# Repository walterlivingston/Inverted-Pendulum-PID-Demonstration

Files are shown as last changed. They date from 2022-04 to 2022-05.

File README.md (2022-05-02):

# Inverted Pendulum PID Demonstration
This was the final project for Applied Mechatronics(MECH 5970) at Auburn University. The project was meant to reflect the four major concepts learned in the class: Sensing, Actuation, Computation, and Mechanical Design.  For this project, an inverted pendulum controlled by a variable PID controller was chosen.  This project was meant to be a demonstration for the professor's Systems & Dynamic Controls(MECH 3140) course.

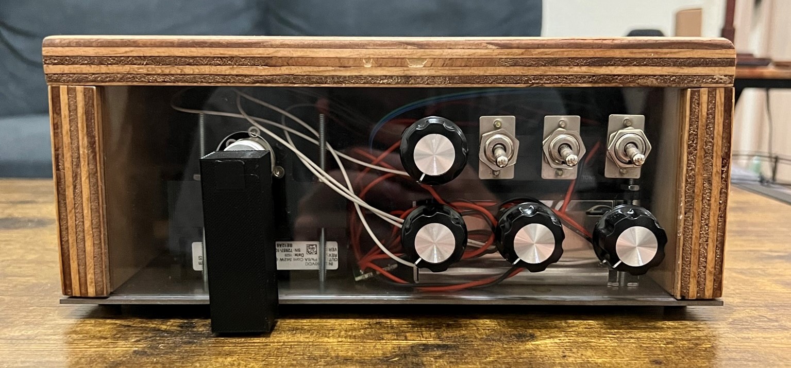
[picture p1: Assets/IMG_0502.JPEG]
Inverted Pendulum Controls Demonstration


## Project Video
Project Video (https://youtu.be/PuW2v3_iuz4)

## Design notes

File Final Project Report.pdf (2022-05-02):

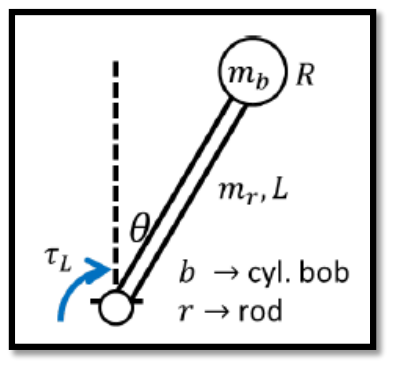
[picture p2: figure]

## Final Project 4: Inverted Pendulum Controls Demonstration

Applied Mechatronics (MECH 5970-019) April 29, 2022
Walter Livingston | Matthew Covington
wbl0009 | mac0139

### Table of Contents

Team Photo | 4
Project Photos | 4
Project Demonstration Video | 7
Functional Summary | 7
Sensing | 7
Actuation | 8
Computation | 8
Mechanical Design | 9
Build Documentation | 10
Schematics and Drawings | 11
Assembly and Part Drawings | 11
LabVIEW Code & Explanation | 11
Improvements | 15
Structural | 15
Functional | 15
Appendix A: Assembly and Part Drawings | 17

### Table of Figures

Figure 1: Team Photo | 4
Figure 2: Front Panel 1 | 4
Figure 3: Front Panel 2 | 5
Figure 4: Back Panel | 5
Figure 5: Internals | 6
Figure 6: IPCD CAD Model | 11
Figure 7: LabVIEW Code | 12
Figure 8: LabVIEW UI | 12
Figure 9: Encoder Processing Snippet | 13
Figure 10: PID Calculations Snippet | 14
Figure 11: Input Filtering Snippet | 14

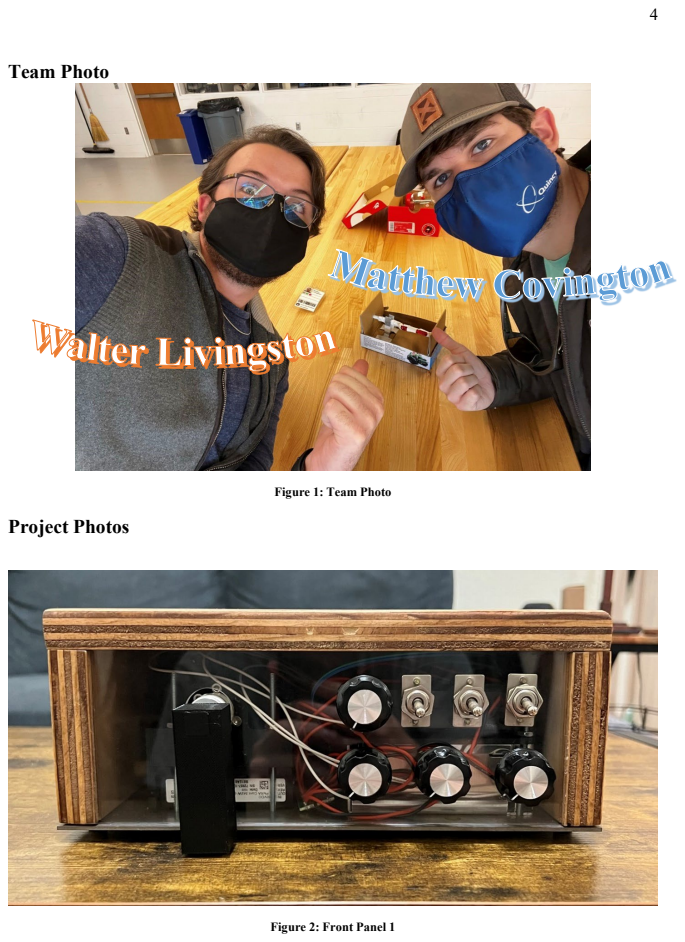
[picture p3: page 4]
Team Photo; Project Photos

Figure 1: Team Photo

Figure 2: Front Panel 1

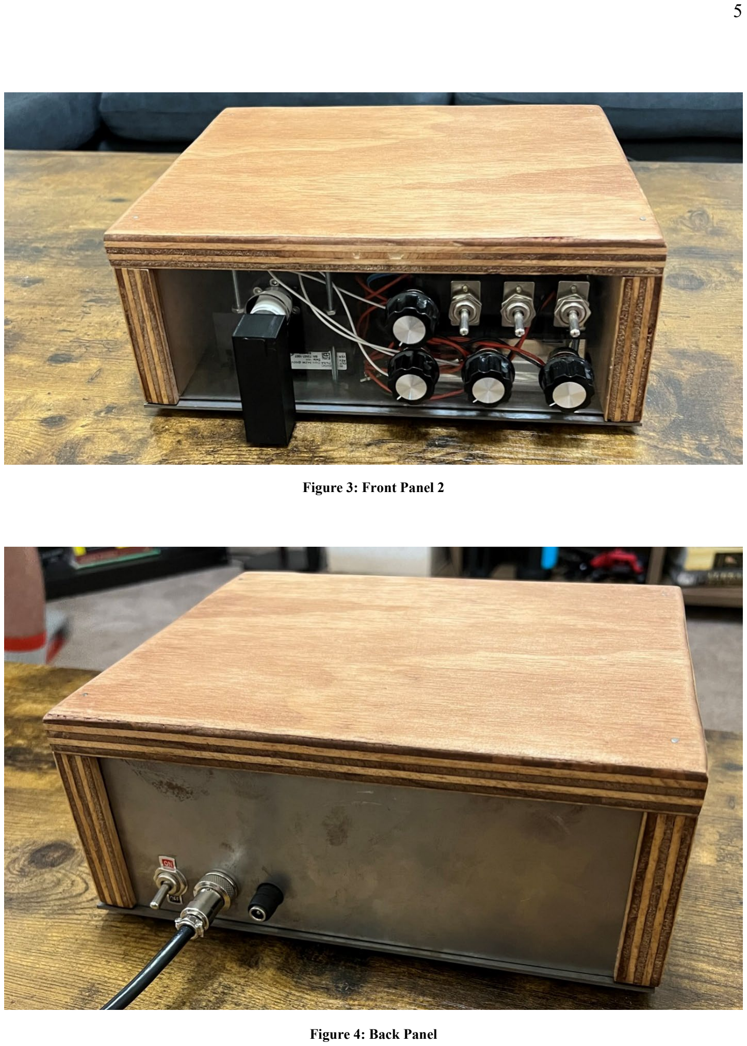
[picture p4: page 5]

Figure 3: Front Panel 2

Figure 4: Back Panel

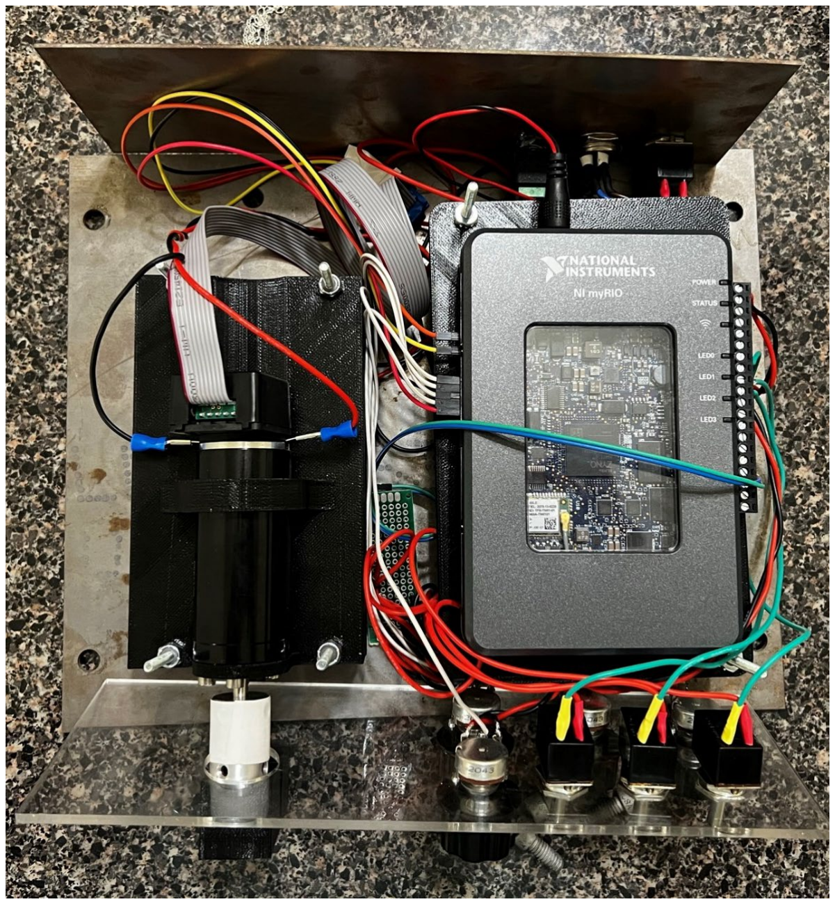
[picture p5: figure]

Figure 5: Internals

### Project Demonstration Video

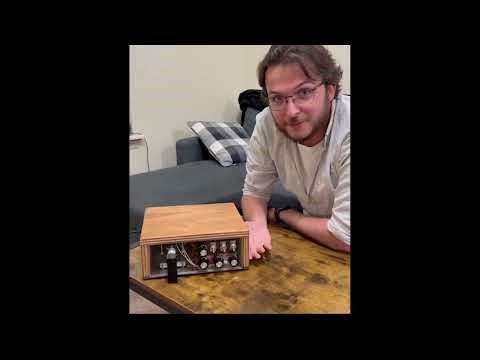
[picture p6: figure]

### Functional Summary

The IPCD’s (Inverted Pendulum Control’s Demonstration) main purpose it to demonstrate the effects of PID control on a dynamic system. This was accomplished by integrating the four founding concepts of this project: Sensing, Actuation, Computation, and Mechanical Design.
Sensing
The primary sensing implementation in this project was a digital encoder. We mounted a HEDL 5540 encoder to the back of the Maxon RE30 24V that will be discussed further in the Actuation section. This encoder had 500 counts per revolution, meaning that the counts had to be read and converted to degrees (or radians). This was accomplished utilizing the NI myRIO 1900 discussed further in Computation. This encoder’s reading acts as the feedback to close the control loop. Every loop of the program read the current angular position of the encoder, processed it based on user-defined gains, and output a control effort to the servo amp.
Another form of sensing in this project comes from the use of potentiometers as part of the user interface. Four potentiometers were used in all: one for the control setpoint, and the other three for the PID gains. A difficulty in this, is given that a potentiometer is an analog device, it is very susceptible to noise. Because the pendulum is meant to be reliable, noise in the user input is unacceptable. To improve reliability within the pendulum’s control, software-based Butterworth filters were used on each input to filter out most noise.

The last form of sensing utilized for this process would be the use of switches. This form of sensing is simplistic as switches are either on or off, and their functionality was written accordingly. If they were on, X happens and if not, Y happens.
Actuation
The actuation implementation within this project was a Maxon RE30 24V motor used in tandem with an AMC Brushless Servo Amp. The motor acts as the torque/control input to the inverted pendulum. The pendulum was mounted about its end to the motor shaft using a coupler. This allowed for sample calculations to be simple given the moment of inertia was comparable to a thin rod rotating about its end.
The servo amp is what allowed the motor to be driven with a -10V/10V analog output from the NI myRIO. The current gain for the amplifier was set at approximately 0.3A/V as this had been tested in Project 3 and provided good results. This gain also simplified the sample calculations, as some of them had already been completed for Project 3.
Computation
The computation in this project was performed by the NI myRIO 1900. This microcontroller uses the LabVIEW programming environment which contains a lot of useful, prebuilt functions for various tasks; some of which are specific to reading and writing from the myRIO. For this project, the National Instruments PID VI (Virtual Instrument) was originally implemented but was eventually replaced by custom PID calculations. The reason for this, is that for a reliable controller design, a full understanding of all the workings of the controller was desired as opposed to a “black box” of controls calculations.
One particular benefit of the myRIO that stands to be noted is its extremely high sampling rate and achievable loop rates. While the generic While Loop within LabVIEW is limited to a 1kHz loop rate, the Real-Time While Loop can achieve rates of up to 1MHz. The importance here is the fact that since digital sensing is used for the feedback loop of the inverted pendulum’s controller. This project is meant to be a demonstration for Dr. Rose’s Systems & Dynamic Control’s course, which deals primarily with the continuous domain. The encoder, and its digital readings, are within the discrete domain. To try and close the gap between these two forms of control, a high loop rate was desirable. The higher the loop rate, the smaller the discretization of readings, and the closer overall the pendulum’s response is to its continuous counterpart.
Within the myRIO programming, many functions and features are established. A general overview of this process is as follows: The myRIO takes in a counter input from the encoder. This counter input is converted to degrees and is compared to the setpoint, as measured by a potentiometer input, and error is calculated. This error is multiplied by a proportional gain, also set by a potentiometer. The derivative of this error is taken and multiplied by a derivative gain set by a potentiometer. The integral of this error is also taken and multiplied by an integral gain set by a potentiometer. With these three gains applied, they’re outputs are all summed together and provided to the Servo Amp as a control effort, or command voltage.

While the above process describes the PID controller used in this project, other features were implemented as well, and controlled by toggle switch inputs. Three additional functions were implemented. The first of which was a frequency input. When this is enabled, the controller outputs a sinusoid with an amplitude of 10 and a frequency set by the setpoint potentiometer. This allows the user to see how various PID gains would affect the frequency response at frequencies between 0 and 2 deg/s. This small range was used to prevent instabilities at all PID gains.
The next function implemented was anti-windup. An integral controller takes the area between the current position and setpoint and uses it to create a control effort to “close the gap.” In cases of large error, this can cause what is called windup. When the integral becomes so large, even when the error is closed, the integral controller is still exhibiting a control effort, which is now no longer decreasing error but increasing it. The anti-windup function reinitializes the integral to zero when it reaches saturation; for this project, saturation is 10/-10 as that is the output of the analog pins utilized on the myRIO.
The last function implemented was controls hold. This switch allows the user to pause the PID gains at their current values and turn the knobs without affect. For instance, if the IPCD is setup with only proportional gain, and the hold switch is turned on. The user can change all of the gains, and the pendulum will still only exhibit a proportional response. But as soon as the hold is turned off, the new gains will take effect and a new response can be observed. Mechanical Design
This project implements a wide variety of concepts lending to the Mechanical Design portion of this project. The first of which would be the mounting method for the motor.
The electrical components were mounted to the base plate of the control module. The base plate is made of 1/8” A36 steel. A 3D printed part was used to secure the DC motor atop the AMC Servo Amp. The part has a hole to allow for the shaft of the motor to pass through so it may be connected to a pendulum. It also has holes through which screws may be placed to ensure the motor does not move. To fasten this part to the base plate, holes in both parts are present, with four 3” bolts passing through both. The AMC Servo Amp is sandwiched between the motor mount and the baseplate, with the 3” bolts passing through the mounting cutouts on the motor driver. The pendulum arm and dowel are 3D printed parts; they are press fit together to allow for a secure connection. A cavity within the pendulum arm allows pennies to be press fit inside it as to raise the moment of inertia, which allows for easier control of the motor position. This cavity allows more weight in the pendulum arm, without making it longer. A coupler is used to connect the pendulum to the shaft of the DC motor.
A similar method is used to mount the myRIO and the power supply. A part was also printed for the myRIO to interface with, with two 3” bolts used to secure this to the mounting plate. The power supply is sandwiched between the motor mount and the baseplate, with the 3” bolts passing through mounting holes on the power supply. Power for the myRIO and the power supply are provided by two power ports mounted to the back plate of the IPCD. The back plate also has an on/off switch mounted to it. The backplate is made of 1/16” aluminum sheet metal.

The front plate is made of 0.117” clear acrylic. This material was used as a means of allowing users to view the inner workings of the IPCD. This front plate houses four potentiometers used as control gain and the position inputs. These are used by the myRIO to determine voltage output (control effort) to the DC motor. Along with potentiometers, toggle switches are also mounted to the front plate. These switches are used as the feature controls mentioned in Computation.
To encapsulate the device, 3/4” AC radiata pine is used for the side walls and top. This material was chosen for aesthetic purposes as the IPCD was meant to look like a vintage stereo. The side pieces are mounted to the base plate via rivet nuts and screws. The rivet nuts were pressure fit into the wood after drilling appropriately sized holes. The screws pass through the baseplate and thread into the rivet nuts, as well as they serve as feet for the device. The top is secure to the side walls by use of wood glue and finishing nails. Each of these pieces have 1/8” wide cutouts which the front and back pieces slide into, ensuring they will not move without having to mount them. This method allows the front and back pieces to be replaced or altered easily.

### Build Documentation

All files and models associated with this project can be found in the following GitHub repository: https://github.com/walterlivingston/Inverted-Pendulum-PID-Demonstration

Schematics and Drawings

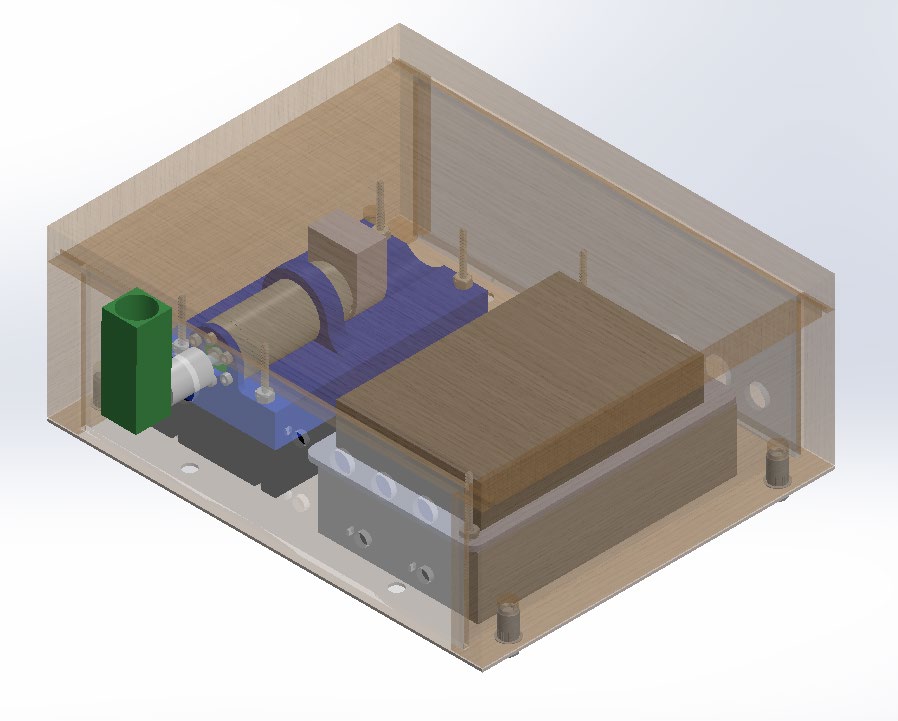
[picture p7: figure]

Figure 6: IPCD CAD Model
Assembly and Part Drawings
The drawing for each assembly (control module, motor mounting assembly, and pendulum) as well as part drawings designed for this project can be found in Appendix A.
LabVIEW Code & Explanation
The code implemented on the myRIO can be seen below in Figure 2. This visual code was written in the LabVIEW Environment. The box around everything here is known as a Real Time While Loop and in this project, was run at a loop rate of 1kHz.

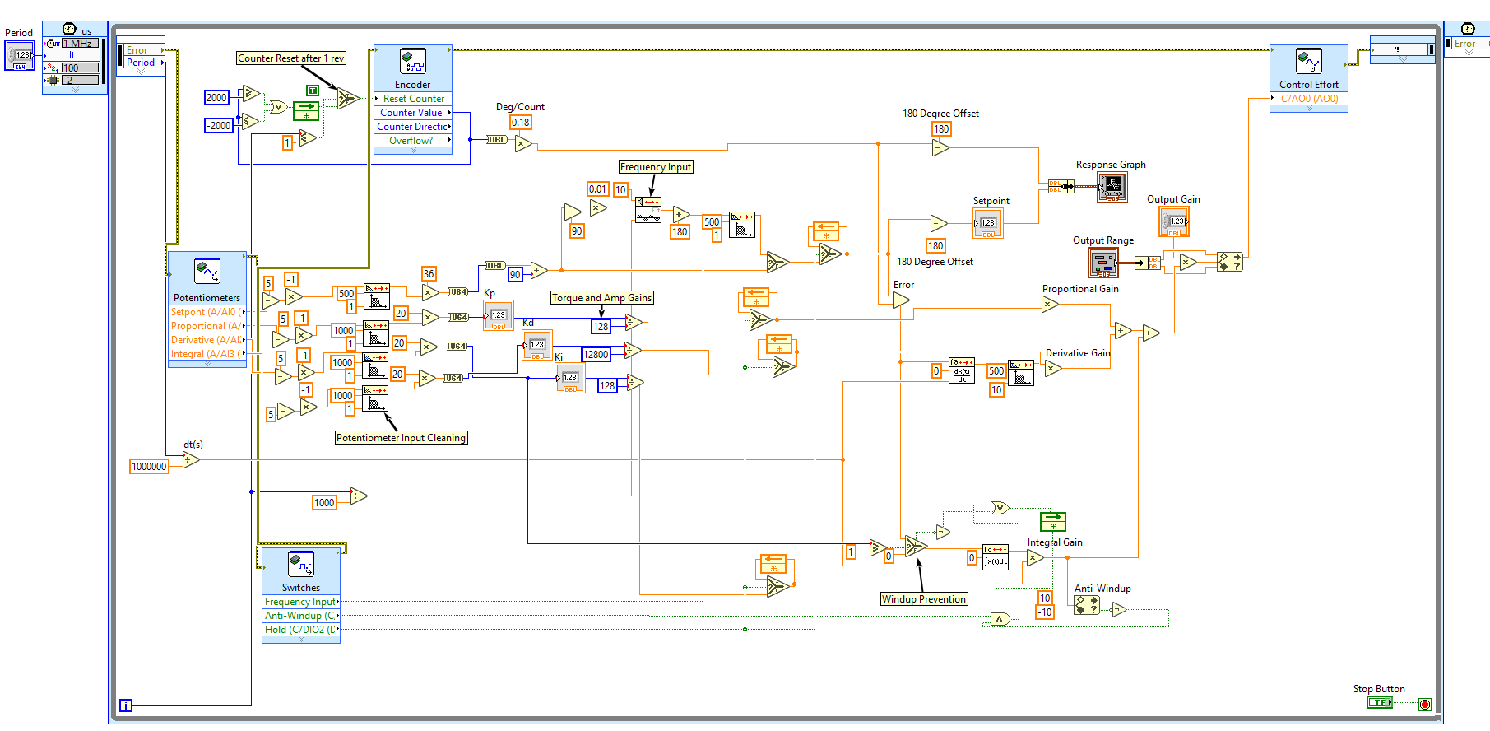
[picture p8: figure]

Figure 7: LabVIEW Code
The UI used to troubleshoot this project can also be seen in Figure 3. This includes a response graph showing the setpoint and the pendulum’s position. It also contains indicators for the setpoint and PID gains. There are controls for an optional output gain (not used in the final version), the period of the loop, and inputs for an output range. These were also useful in troubleshooting the code shown above in Figure 2.

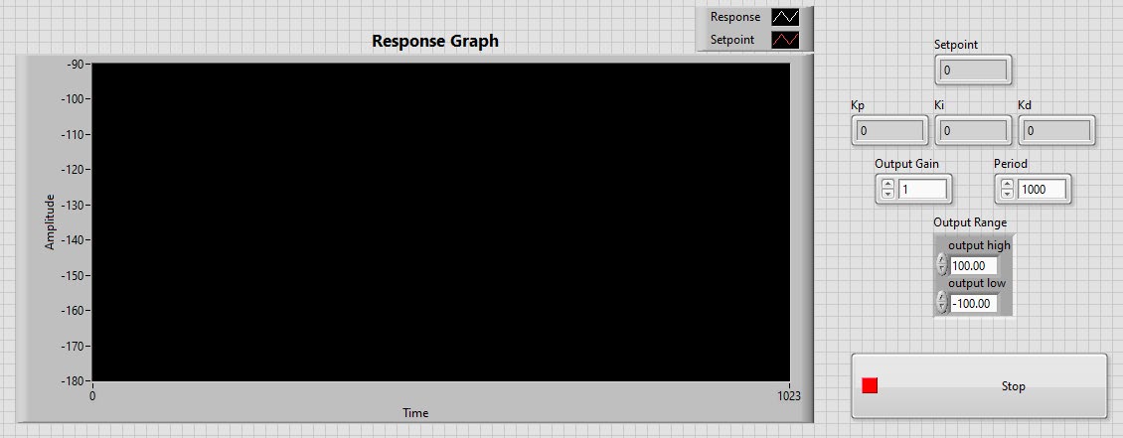
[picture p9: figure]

Figure 8: LabVIEW UI
The encoder readings were handled by the code snippet shown in Figure 4. This takes the encoder value and compares it to -/+ 2000. The reason for this is the HEDL 5400 encoder used in this project has a counts per revolution of 500. This being a quadrature encoder, that means that the myRIO is reading 4 times the counts per revolution, that being 2000. This comparison tells the myRIO to reset the counter if the encoder has gone a full revolution. It can also be seen her that something is being compared to the number 1. This is the index of the while loop. This bit of code tells the myRIO to reset the encoder counter if this is the first iteration of the while loop. Lastly, the encoder counts are also multiplied by 0.18 which is a conversion from counts to degrees.

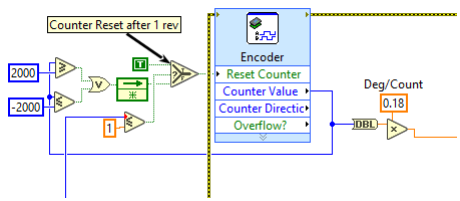
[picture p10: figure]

Figure 9: Encoder Processing Snippet
The PID controls calculations were handled by the code snippet shown in Figure 5. At the top of this figure, error is calculated from the setpoint and the encoder input, and passed into the P, I, and D components of controller. The proportional component is labeled in Figure 5, and is a simple multiplication of error by a gain. The derivative component is labeled and is shown in the middle of the figure. This uses the LabVIEW PtByPt Derivate VI as well as the PtByPt Butterworth Filter VI. The reason for this, is a PtByPt Derivative contains a lot of noise which would lead to instabilities in the control effort. It then multiplies this filtered derivative by a gain. Lastly the integral component is labeled and is shown at the bottom of the figure. It takes in the error and utilizes the PtByPt Integral VI to get the integral of the error. This is then multiplied by a gain and all three components are summed and passed to the analog out of the myRIO.

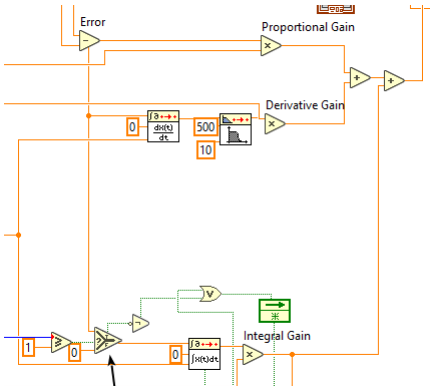
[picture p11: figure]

Figure 10: PID Calculations Snippet
The filtering and processing of the potentiometer inputs are shown in Figure 6. First, all inputs had 5 subtracted from them and were multiplied by 1. This was because the potentiometers inputs were between 0 and 5V, but because of their orientation, this range was reversed. This subtraction and multiplication rectified that. All the inputs are then filtered by the PtByPt Butterworth Filter, and they are multiplied by the conversion factors. For the setpoint, a range of -90 to 90 was desired, while for the gains, a range of 0 to 100 was desired. These values are then cast to integers to attain clean, non-floating-point values and the gains are further processed with another conversion factor. They are divided by the number 128 as this is a product of the motor’s torque constant and the servo amps voltage gain. The derivative gain’s conversion is actual 12800 as the pendulum requires very small derivative gains to remain stable.

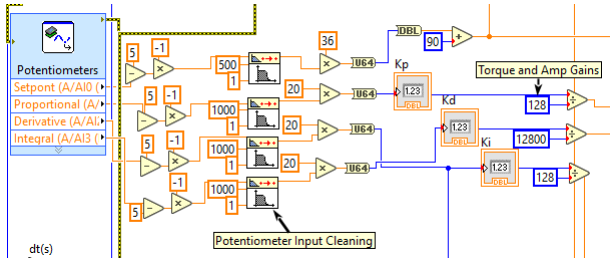
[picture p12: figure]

Figure 11: Input Filtering Snippet

### Improvements

Structural
The structure of the IPCD is rigid and compact, although this does bring up some issues. The device would have been easier to work with if the tolerances between the internal components and the front and back plates were larger. Due to these tight tolerances, wires were jumbled and would often get in the way. Another issue with the front and back plate is with the depth of the slots in the wood which these parts are inserted. The slots are slightly too deep, part of this can be contributed to the plywood not being quite 3/4" thick. If the actual size were considered this issue would have been avoided. Because the back piece is thinner than the slots, it is able to move. To minimize this movement, the wood side pieces were slanted inwards slightly.
Taking the wood exterior pieces off is simple, however the nut/bolt connection could be improved. The use of river nuts is because initially the plan was to use more sheet metal parts so these nuts would allow for loosening of the bolts without having access to the nut, as it would be inside the IPCD. A better alternative would be threaded inserts, as they have external threads for mounting. Currently, the rivet nuts used do not have a way to solidify their connection to the wood, the use of the proposed inserts would contain a solid connection.
The pendulum arm is short enough that the device can sit on the table without having to hang the pendulum over the edge, however, it still may be too long. At high angular, the pendulum has the potential to come into contact with the set point knob. If the system were given gains that would make it unstable, the user’s hand could cross the pendulum’s path, resulting in some pain as this motor is powerful. The issue with the length of the pendulum could be solved in one of two ways: make the pendulum shorter or shift the motor mounting assembly much closer to the wall, there is up to 5/8” of room between the motor mounting assembly and the wooden side wall.
Functional
The IPCD works really well and was an overall successful project. There were many aspects, that in hindsight, the team would’ve changed. The first of these changes would be the use of an analog position sensor rather than a digital encoder. There are a few reasons for this, the primary of which being that the pendulum’s zero is reset every time the myRIO is power cycled. If the pendulum is not point straight down, when the myRIO is powered on, the zero position is offset. An analog sensor would not have this issue. An analog position sensor would also make the IPCD more analogous to a continuous sensor, where the digital is by nature discrete.
Another functional improvement would be the addition of a screen to display the response of the pendulum as it happens. The frequency input switch is useful to display the frequency response, but it is clearer to see how different gains affect the response using a scope such as the one shown in Figure 3. The team had plans to do this through a serial connection with an Arduino Nano, and the screen Dr. Rose had purchased, but there was not enough time to implement this.

The last functional improvement would be a manual controls mode. By this, I mean a pin header on the rear of the pendulum and a switch to toggle this controls mode. This would allow students to develop their own PID controller and test it on this pendulum. Aside from the analog position sensor, this would be the largest improvement to the project. With this addition, not only would the IPCD be useful for Systems & Dynamic Controls as a demonstration, but would also be useful for Applied Mechatronics projects 2 and 3.

### Appendix A: Assembly and Part Drawings

The drawing order is as follows:
- Control Module Assembly
- Base Plate
- Motor Mount Assembly
- Motor Mount
- Wood Side Piece
- Wood Top Piece
- Front Piece
- Back Piece
- Pendulum Assembly
- Pendulum
- Pendulum Dowel
- myRio Mounting Plate

B | B

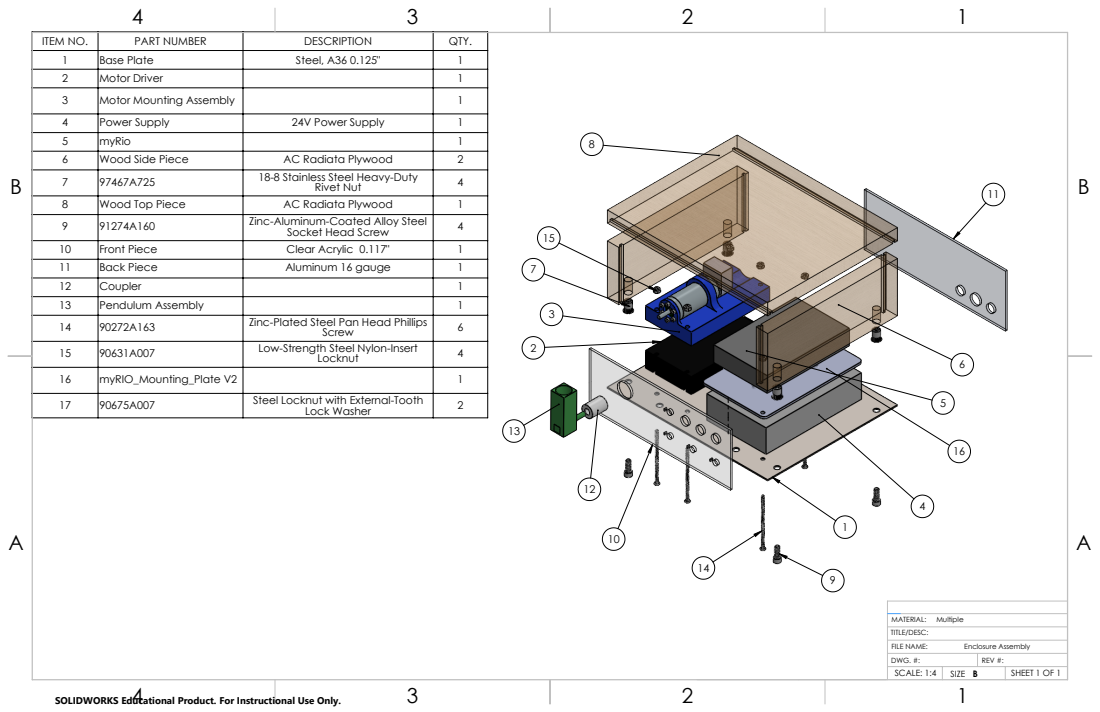
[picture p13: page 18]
Multiple; TITLE/DESC: FILE NAME:; MATERIAL:; Enclosure Assembly

ITEM NO. | PART NUMBER | DESCRIPTION | QTY.
1 | Base Plate | Steel, A36 0.125" | 1
2 | Motor Driver | | 1
3 | Motor Mounting Assembly | | 1
4 | Power Supply | 24V Power Supply | 1
5 | myRio | | 1
6 | Wood Side Piece | AC Radiata Plywood | 2
7 | 97467A725 | 18-8 Stainless Steel Heavy-Duty Rivet Nut | 4
8 | Wood Top Piece | AC Radiata Plywood | 1
9 | 91274A160 | Zinc-Aluminum-Coated Alloy Steel Socket Head Screw | 4
10 | Front Piece | Clear Acrylic 0.117" | 1
11 | Back Piece | Aluminum 16 gauge | 1
12 | Coupler | | 1
13 | Pendulum Assembly | | 1
14 | 90272A163 | Zinc-Plated Steel Pan Head Phillips Screw | 6
15 | 90631A007 | Low-Strength Steel Nylon-Insert Locknut | 4

16 | myRIO_Mounting_Plate V2 | | 1
17 | 90675A007 | Steel Locknut with External-Tooth Lock Washer | 2

DWG. #: | REV #:
SCALE: 1:4 | SIZE B | SHEET 1 OF 1

SOLIDWORKS Educational Product. For Instructional Use Only.

B

B

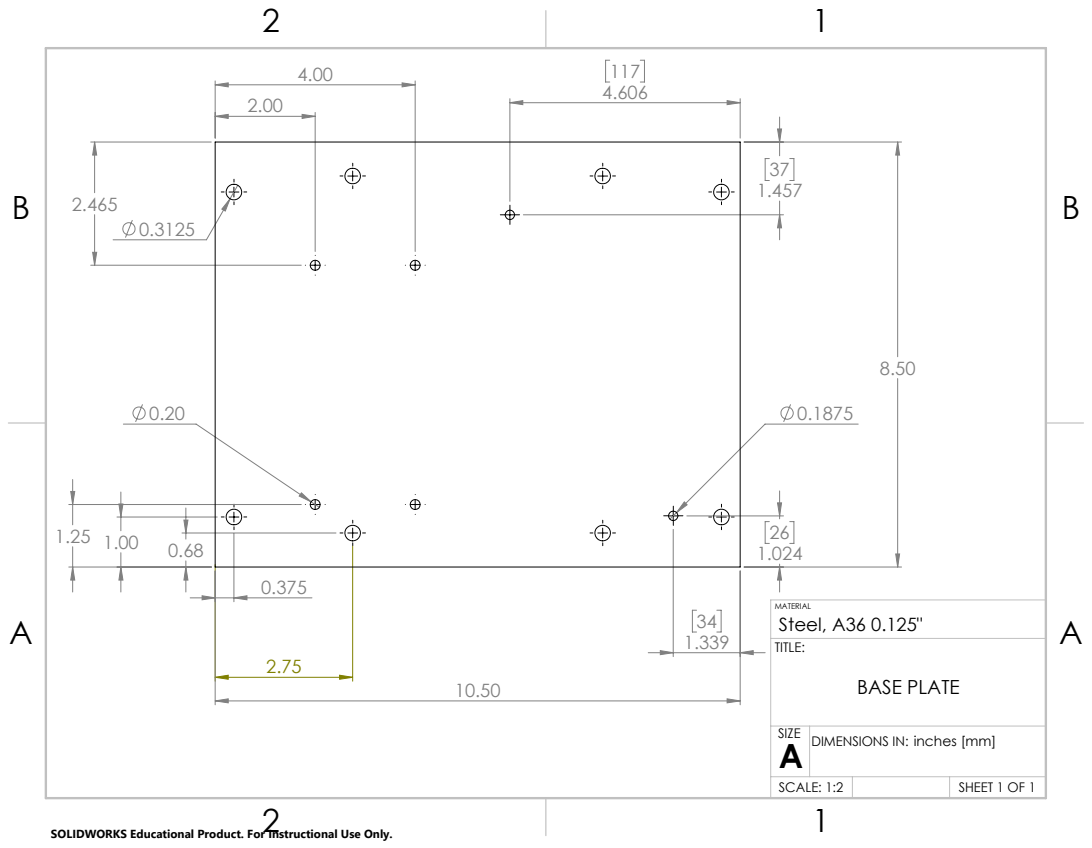
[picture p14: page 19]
TITLE:; MATERIAL; BASE PLATE; Steel, A36 0.125"

SIZE | DIMENSIONS IN: A inches [mm]

SCALE: 1:2 | | SHEET 1 OF 1

B

B

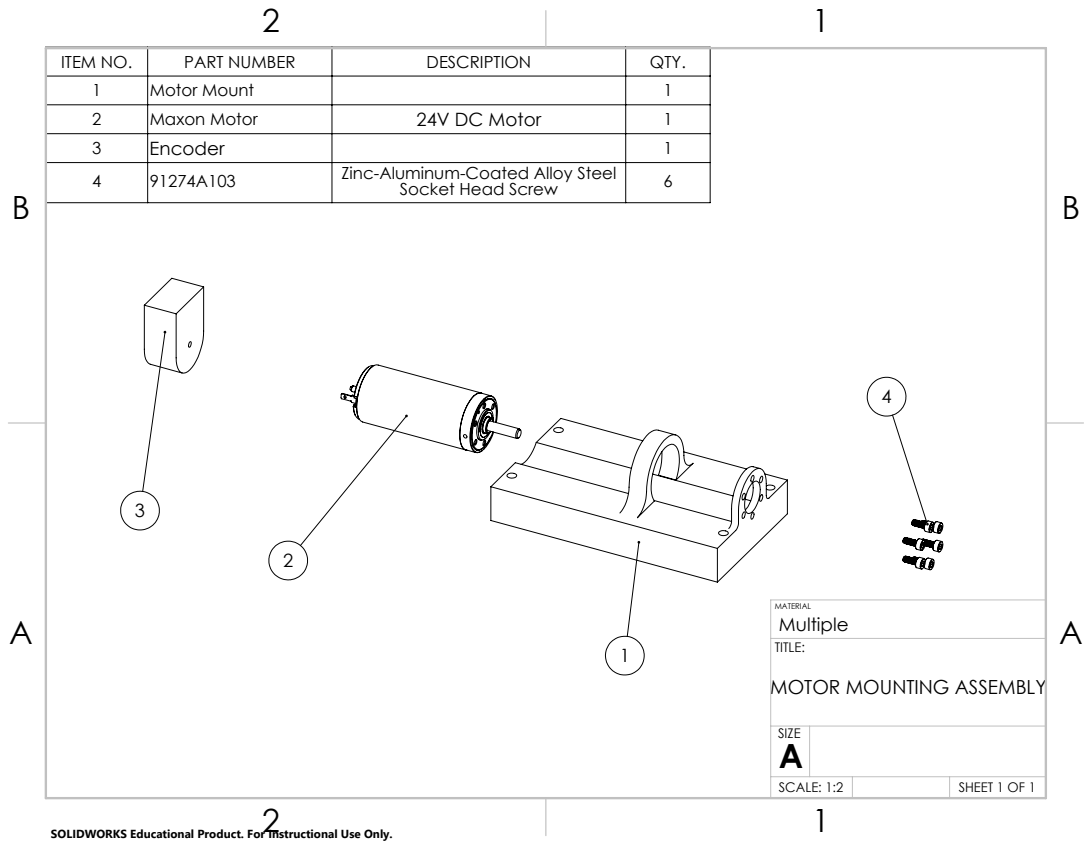
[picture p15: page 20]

ITEM NO. | PART NUMBER | DESCRIPTION | QTY.
1 | Motor Mount | | 1
2 | Maxon Motor | 24V DC Motor | 1
3 | Encoder | | 1
4 | 91274A103 | Zinc-Aluminum-Coated Alloy Steel Socket Head Screw | 6

MATERIAL
Multiple
TITLE:
MOTOR MOUNTING ASSEMBLY

SIZE A

SCALE: 1:2 | SHEET 1 OF 1

B

B

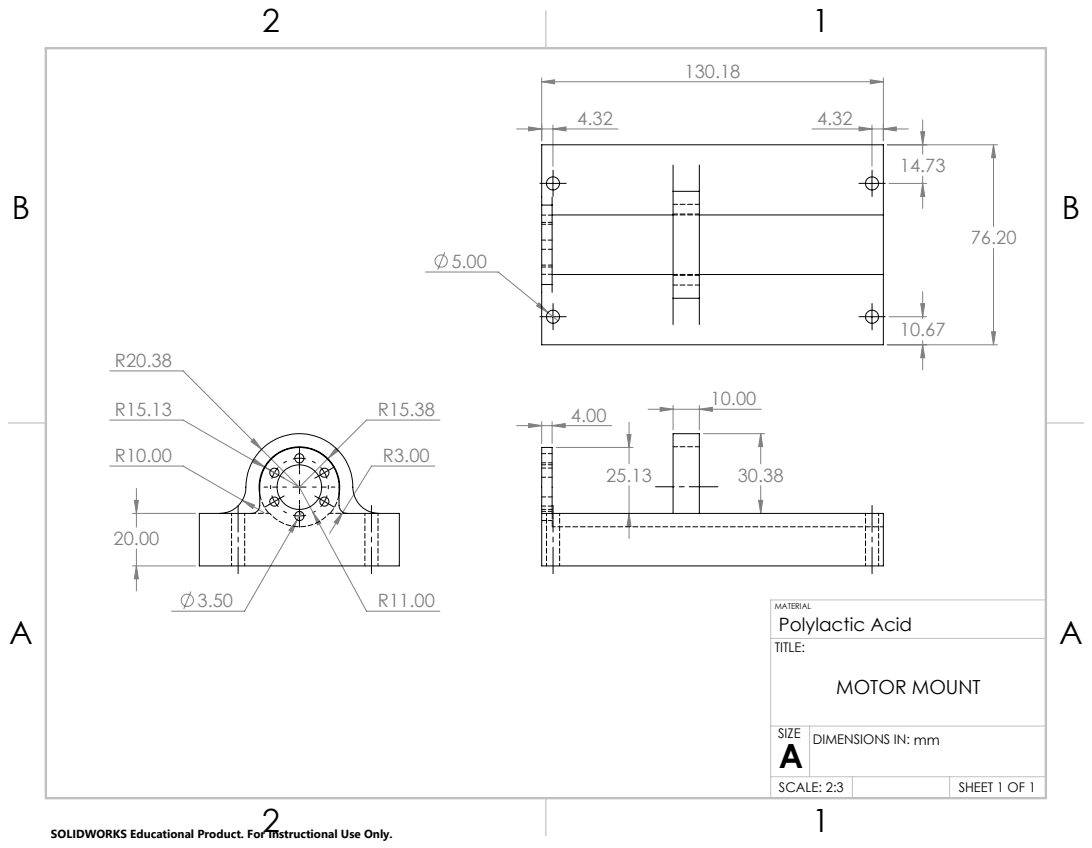
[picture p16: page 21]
TITLE:; MATERIAL; MOTOR MOUNT; Polylactic Acid

SIZE | DIMENSIONS IN: A mm

SCALE: 2:3 | | SHEET 1 OF 1

B

B

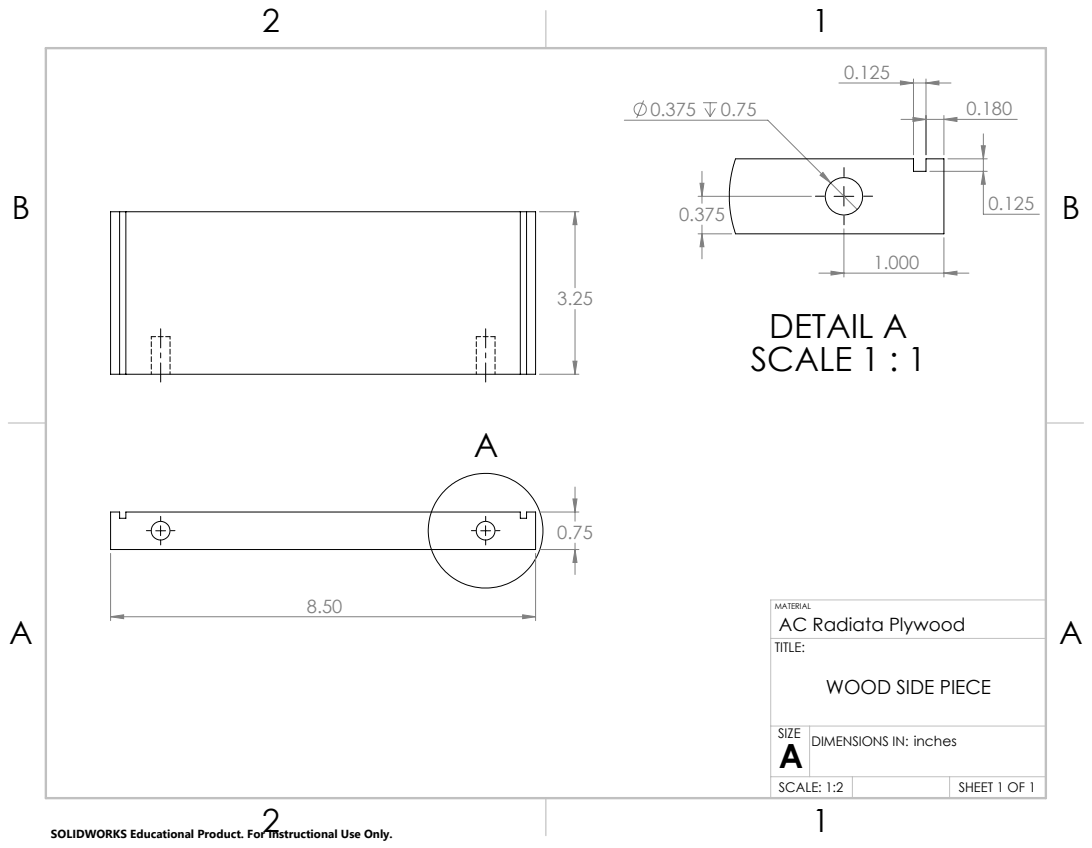
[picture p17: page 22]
1.000 DETAIL A SCALE 1 : 1

MATERIAL
AC Radiata Plywood
TITLE:
WOOD SIDE PIECE

SIZE | DIMENSIONS IN: A inches

SCALE: 1:2 | | SHEET 1 OF 1

B

B

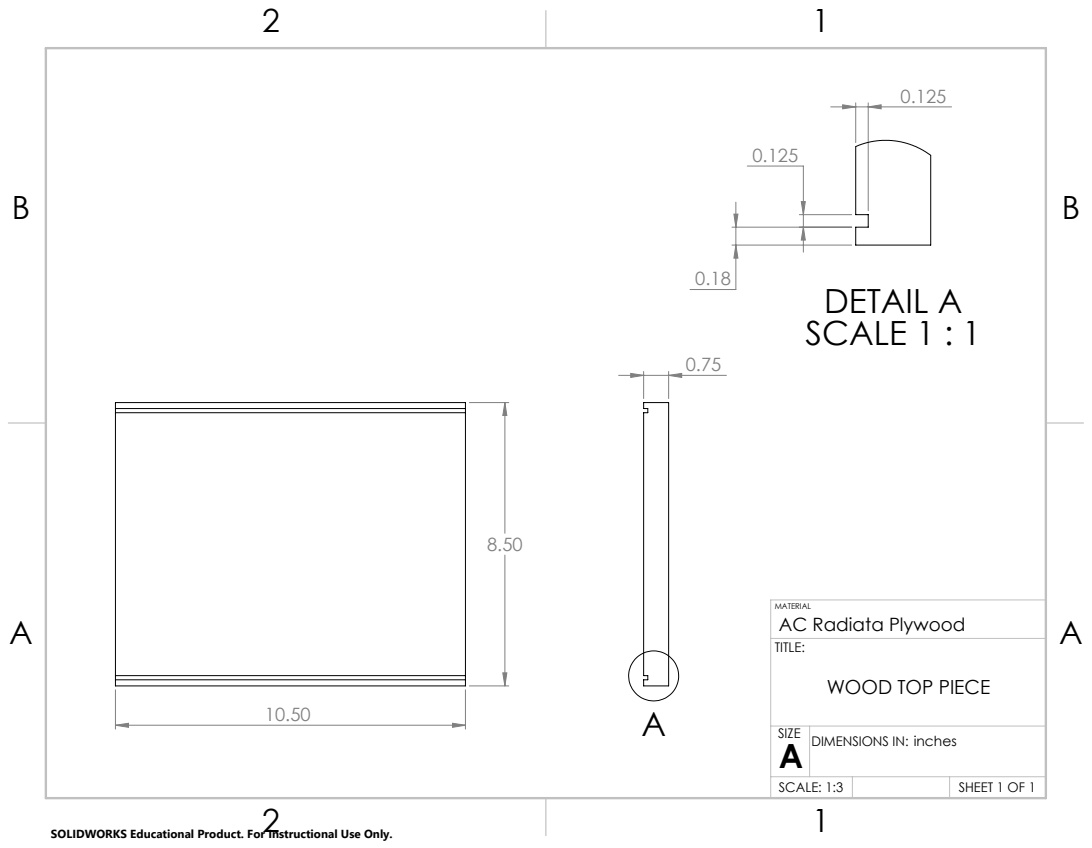
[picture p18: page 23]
DETAIL A SCALE 1 : 1

MATERIAL
AC Radiata Plywood
TITLE:
WOOD TOP PIECE

SIZE | DIMENSIONS IN: A inches

SCALE: 1:3 | | SHEET 1 OF 1

B

B

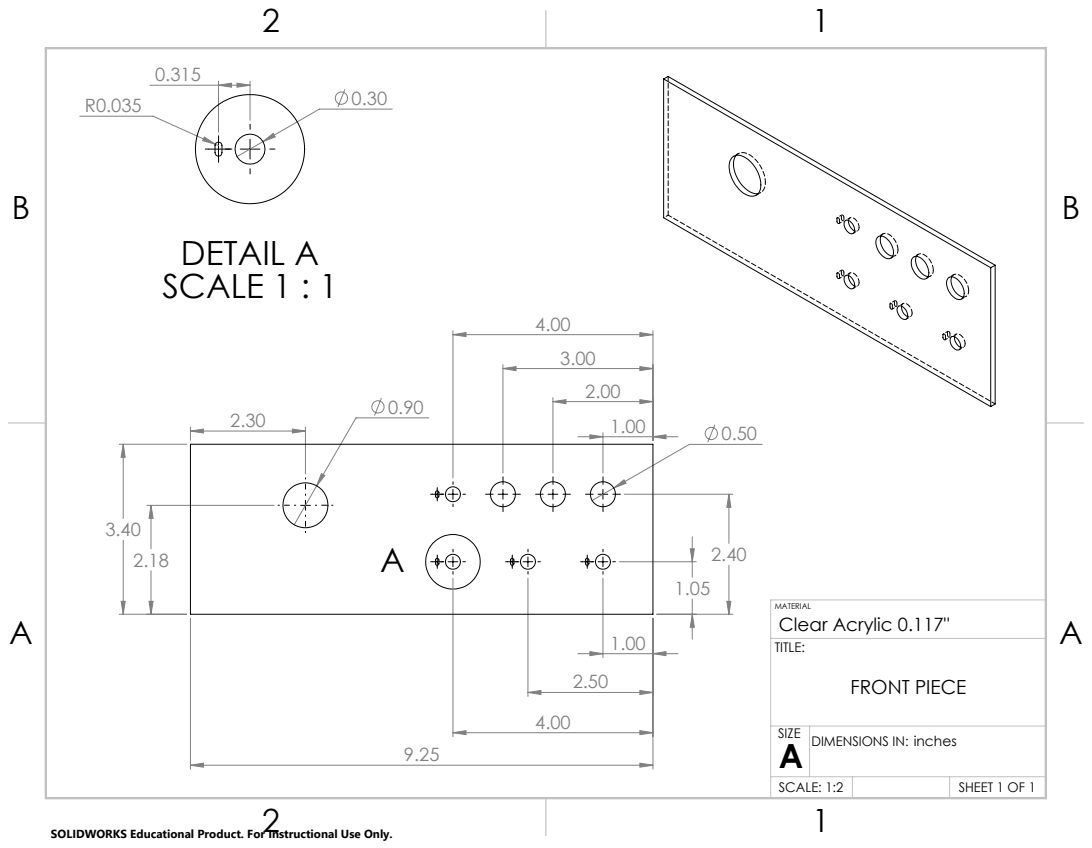
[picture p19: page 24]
DETAIL A SCALE 1 : 1; TITLE:; MATERIAL; FRONT PIECE; Clear Acrylic 0.117"

SIZE | DIMENSIONS IN: A inches

SCALE: 1:2 | | SHEET 1 OF 1

B

B

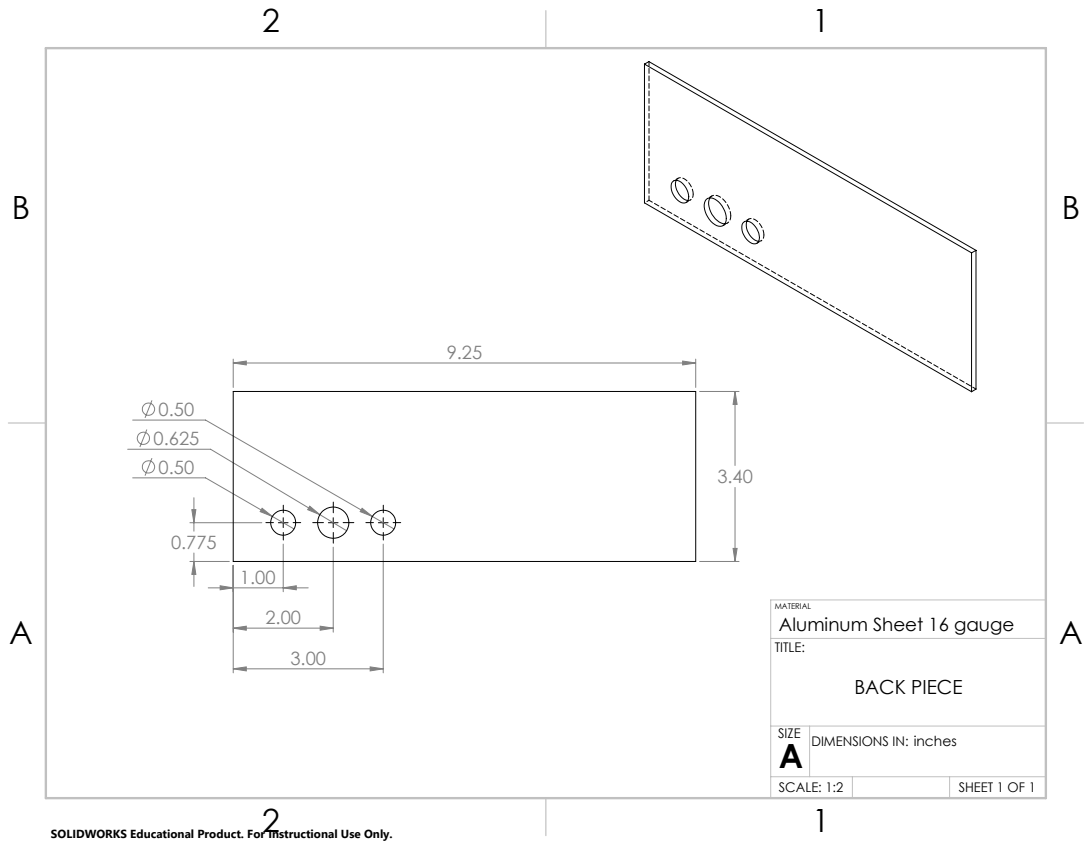
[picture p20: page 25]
BACK PIECE

MATERIAL
Aluminum Sheet 16 gauge
TITLE:

SIZE | DIMENSIONS IN: A inches

SCALE: 1:2 | | SHEET 1 OF 1

B

B

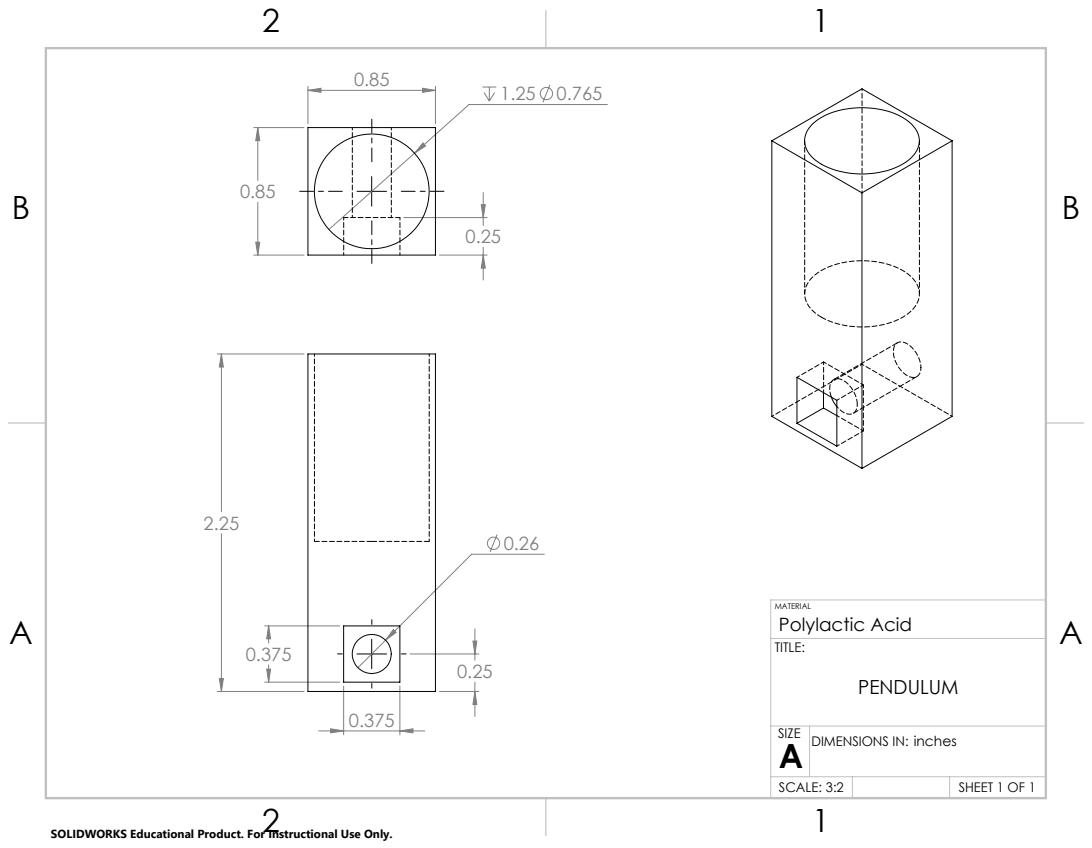
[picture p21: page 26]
TITLE:; MATERIAL; PENDULUM; Polylactic Acid

SIZE | DIMENSIONS IN: A inches

SCALE: 3:2 | | SHEET 1 OF 1

B

B

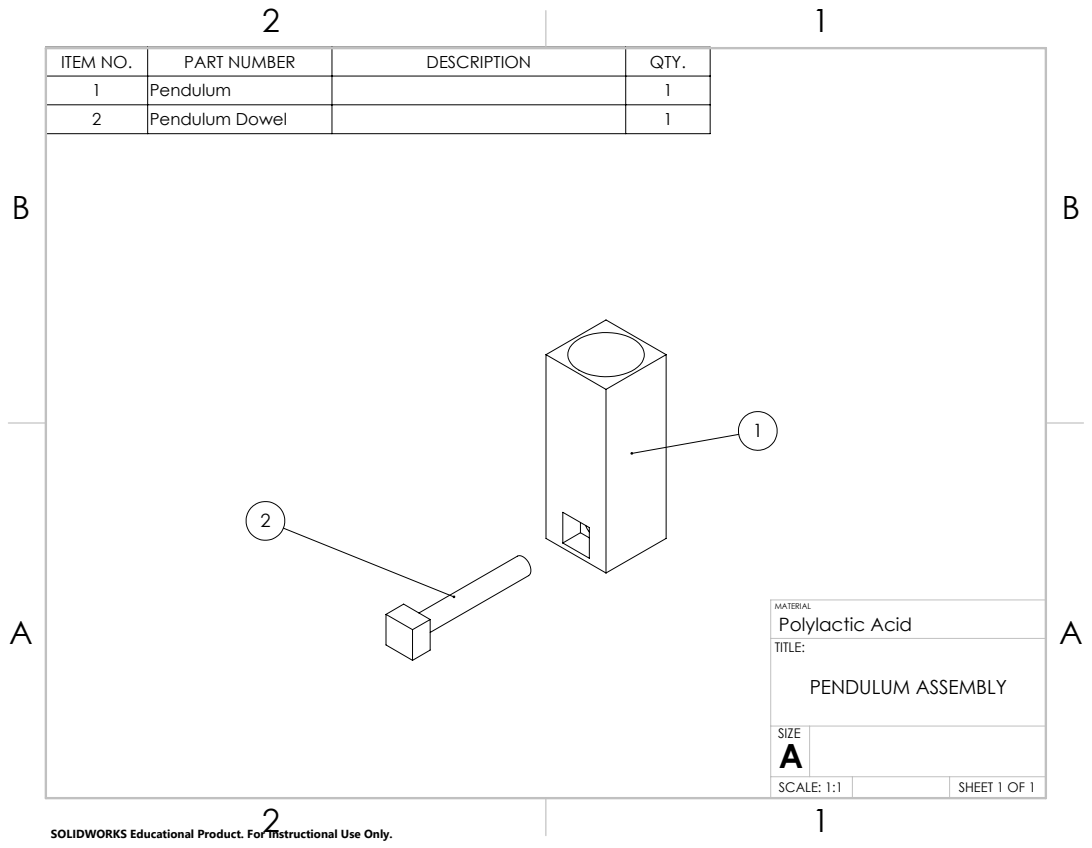
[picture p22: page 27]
TITLE:; MATERIAL; PENDULUM ASSEMBLY; Polylactic Acid

ITEM NO. | PART NUMBER | DESCRIPTION | QTY.
1 | Pendulum | | 1
2 | Pendulum Dowel | | 1

SIZE A

SCALE: 1:1 | SHEET 1 OF 1

B

B

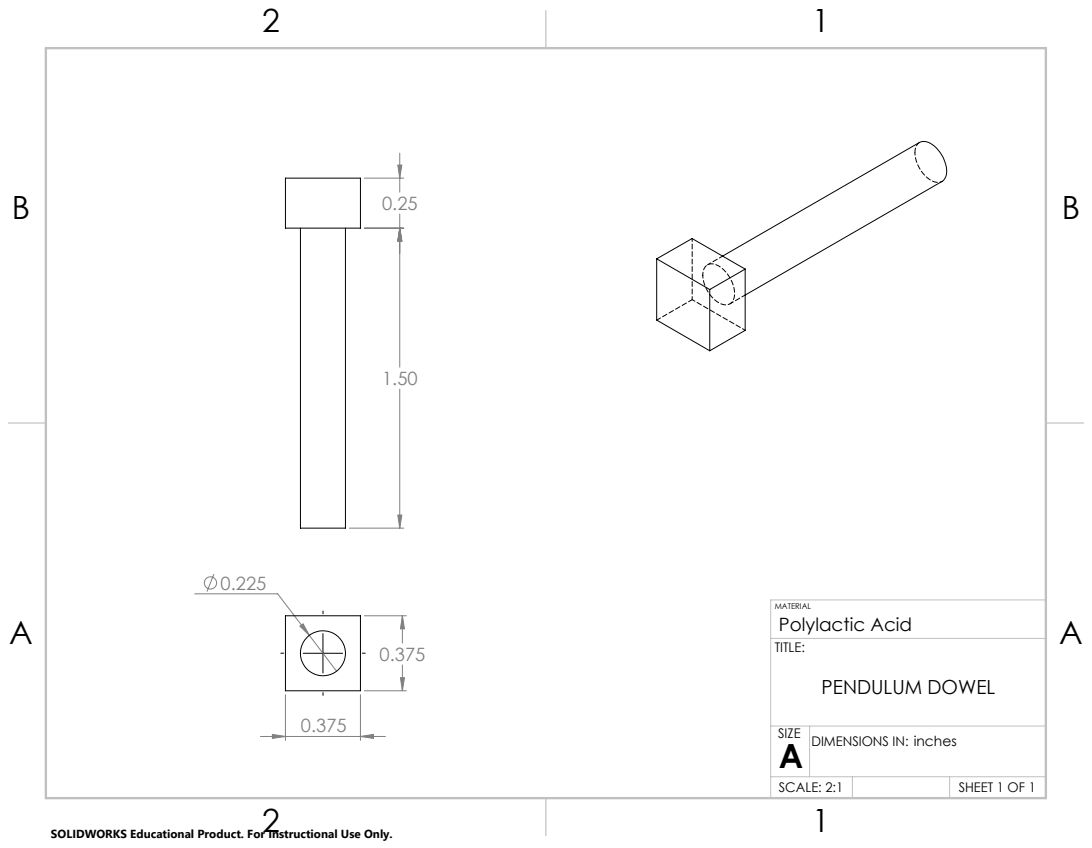
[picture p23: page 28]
TITLE:; MATERIAL; PENDULUM DOWEL; Polylactic Acid

SIZE | DIMENSIONS IN: A inches

SCALE: 2:1 | | SHEET 1 OF 1

B

B

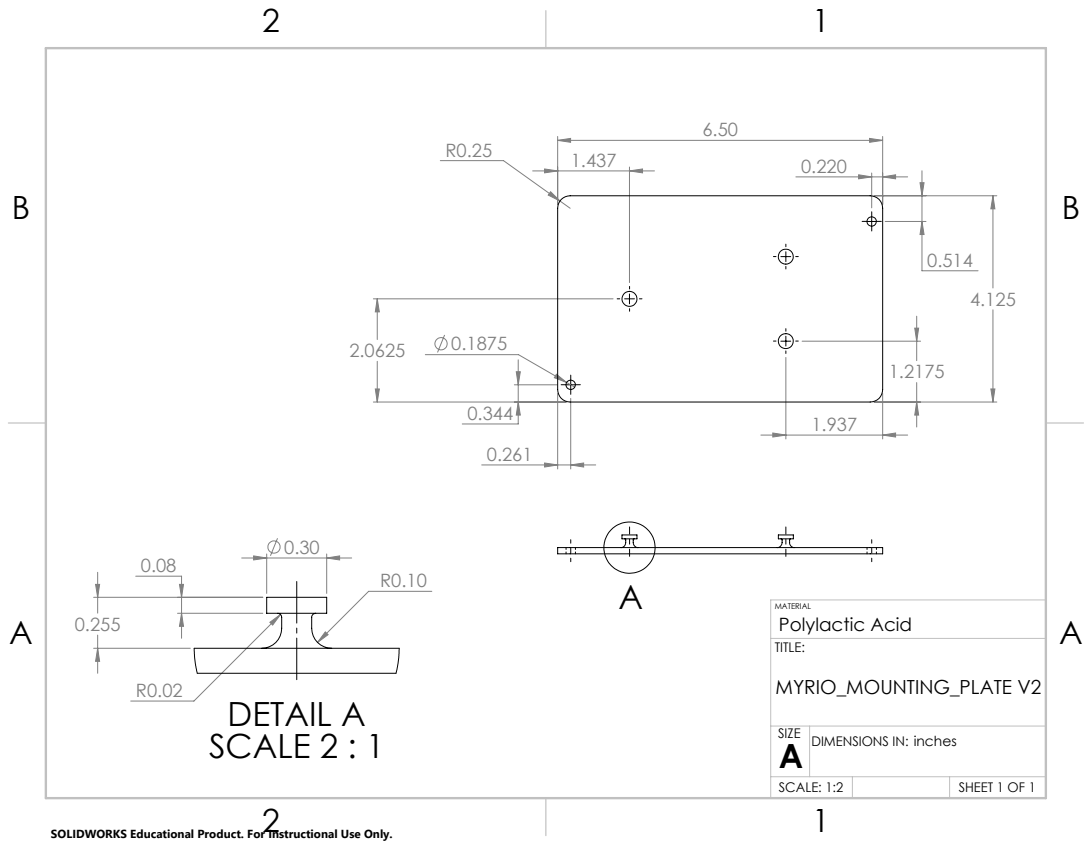
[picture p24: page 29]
DETAIL A; SCALE 2 : 1; SIZE; TITLE:; MATERIAL; MYRIO_MOUNTING_PLATE V2; Polylactic Acid

DIMENSIONS IN: A inches

SCALE: 1:2 | | SHEET 1 OF 1

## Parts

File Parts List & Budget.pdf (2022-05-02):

Part | Quantity | Part # | Cost ($)/Quantity | Total Cost ($) | Link/Source
Potentiometers | 6 | COM-14622 | $ 1.60 | $ 9.60 | https://www.sparkfun.com/products/14622
LCD Screen | 1 or 2 | LCD-16009 | $ 33.95 | $ 33.95 | https://www.sparkfun.com/products/16009
Motor w/ Encoder | 1 or 2 | 4882 | $ 34.95 | $ 34.95 | https://www.pololu.com/product/4882
Assorted Pot Knobs | 1 set | B00NN6M1V4 | $ 9.99 | $ 9.99 | https://www.amazon.com/Adjustable-Rotate-Button-Potentiometer-Control/dp/B00NN6M1V4
12V AC to DC Power Supply | 1 | TOL-16266 | $ 25.95 | $ 25.95 | https://www.sparkfun.com/products/16266
Motor Driver | 1 | 3142 | $ 49.95 | $ 49.95 | https://www.pololu.com/product/3142
12V to 5V Converter | 1 | 2843 | $ 4.95 | $ 4.95 | https://www.pololu.com/product/2843
Cannon Connectors | 2 | PRT-11475 | $ 3.95 | $ 7.90 | https://www.sparkfun.com/products/11475
Stainless Steel Twist-Resistant Rivet Nuts (1/4"-20 thread) | 4, comes with 10 | 97467A725 | $11.43/10 Nuts | $ 11.43 | https://www.mcmaster.com/nuts/rivet-nuts/stainless-steel-twist-resistant-rivet-nuts/
Steel Sheet .062" thick | ~240 in^2 | 3DRW8 | $0.10/in^2 | $ 24.00 | BK Metal Shop (https://spider.eng.auburn.edu/makerspace/materials.php)
Aluminum Socket Head Screw (1/4"-20 Thread Size, 5/8" Long) | 4, comes with 5 | 98511A621 | $17.84/5 Screws | $ 17.84 | https://www.mcmaster.com/98511A621
Zinc-Aluminum-Coated Alloy Steel Socket Head Screw (1/4"-20 Thread Size, 5/8" Long) | 4, comes with 50 | 91274A160 | $10.15/50 Screws | $ 10.15 | https://www.mcmaster.com/91274A160
The Highlighted Row is an alternative screw. It would be cheaper by $7.69 and
come with 50 screws instead of 5 screws.

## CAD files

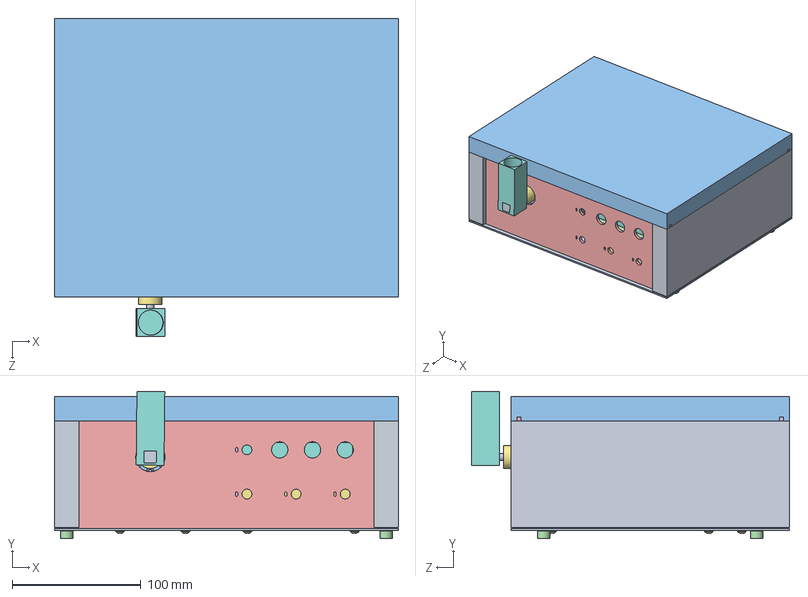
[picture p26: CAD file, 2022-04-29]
Enclosure Mk 4/Enclosure Assembly.SLDASM
266.7 x 114.2 x 246.6 mm
Base Plate
Driver Block
Motor Mount
Maxon Motor
Encoder Block
91274A103_Zinc-Aluminum-Coated Alloy Steel Socket Head Screw x 6
Power Supply Block
myRio Block
Wood Side Piece x 2
97467A725_18-8 Stainless Steel Heavy-Duty Rivet Nut x 4
Wood Top Piece
91274A160_Zinc-Aluminum-Coated Alloy Steel Socket Head Screw x 4
Front and Back Piece
Back Piece
Coupler
Pendulum
Pendulum Dowel
90272A163_Zinc-Plated Steel Pan Head Phillips Screw x 6
90631A007_Low-Strength Steel Nylon-Insert Locknut x 4
myRIO_Mounting_Plate V2
90675A007_Steel Locknut with External-Tooth Lock Washer x 2

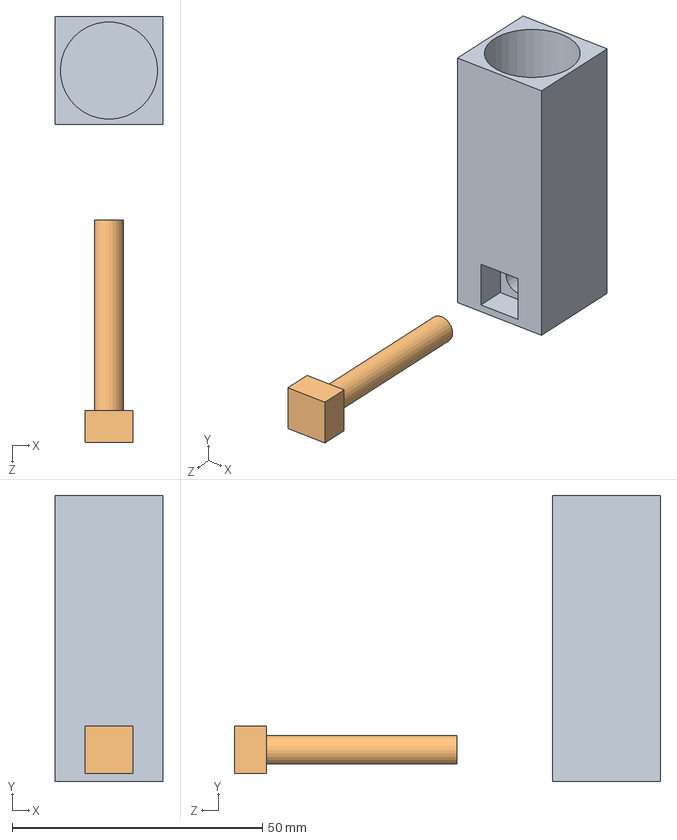
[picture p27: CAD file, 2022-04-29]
Enclosure Mk 4/Pendulum Assembly.SLDASM
21.6 x 57.1 x 85.1 mm
Pendulum
Pendulum Dowel

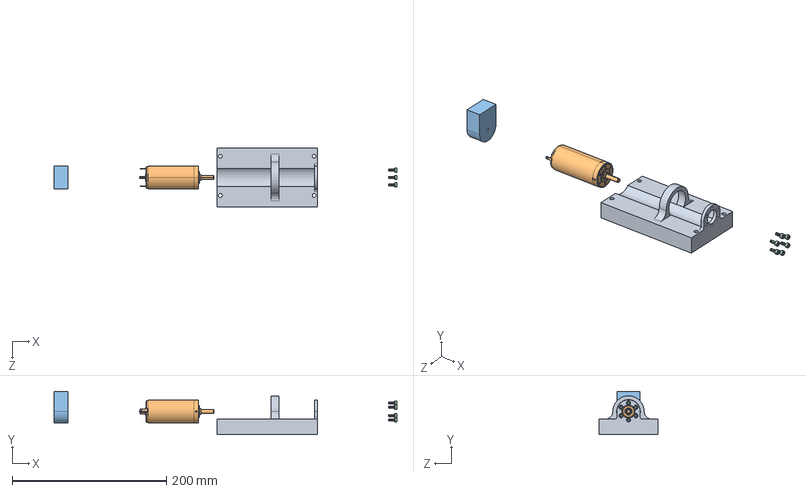
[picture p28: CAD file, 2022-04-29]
Enclosure Mk 4/Motor Mounting Assembly.SLDASM
444.4 x 56.1 x 76.2 mm
Motor Mount
Maxon Motor
Encoder Block
91274A103_Zinc-Aluminum-Coated Alloy Steel Socket Head Screw x 6

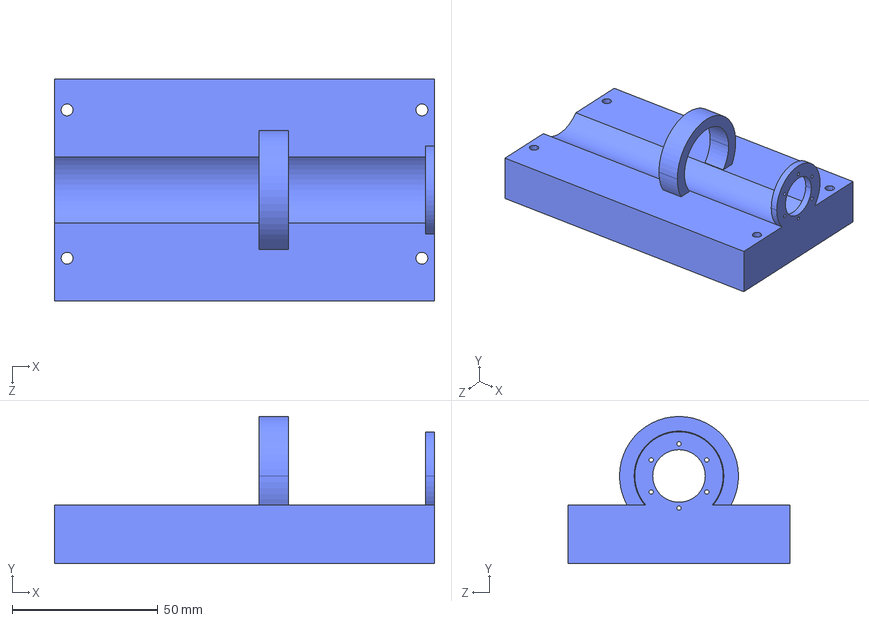
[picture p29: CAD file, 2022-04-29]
Enclosure Mk 4/3D Printed Parts/Motor Mount.STEP
130.2 x 50.4 x 76.2 mm

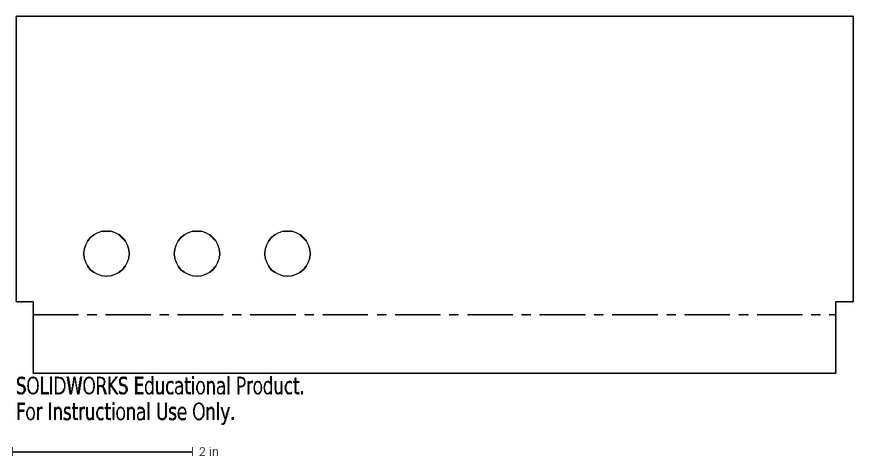
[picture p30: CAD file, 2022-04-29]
Enclosure Mk 4/DXF Files/Flat pattern - Back Plate (with Bend).DXF
SOLIDWORKS Educational Product.
For Instructional Use Only.

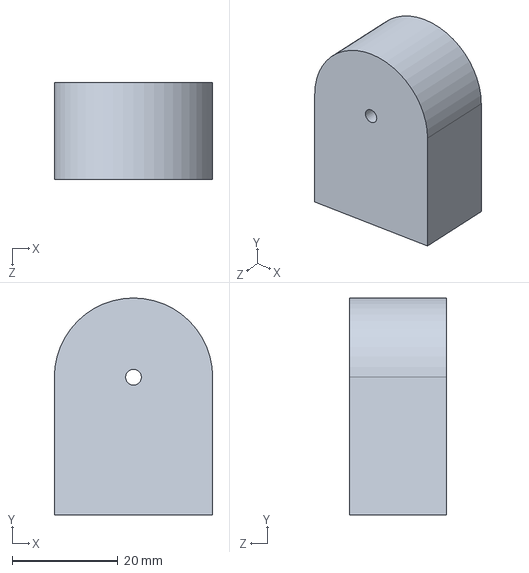
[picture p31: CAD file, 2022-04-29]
Enclosure Mk 4/Encoder Block.SLDPRT
30.0 x 41.1 x 18.3 mm

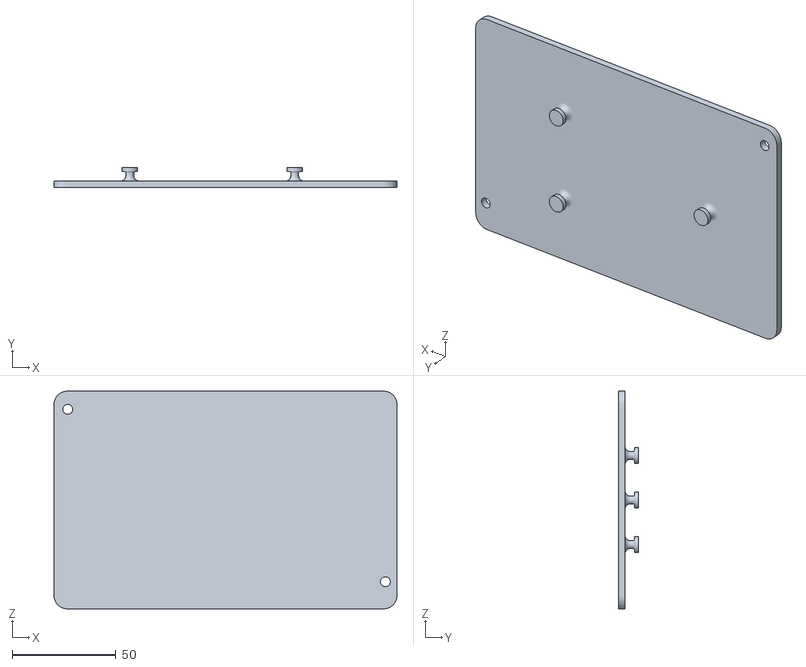
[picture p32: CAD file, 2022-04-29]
Enclosure Mk 4/3D Printed Parts/myRIO_Mounting_Plate V2.STL
165.1 x 9.65 x 104.8

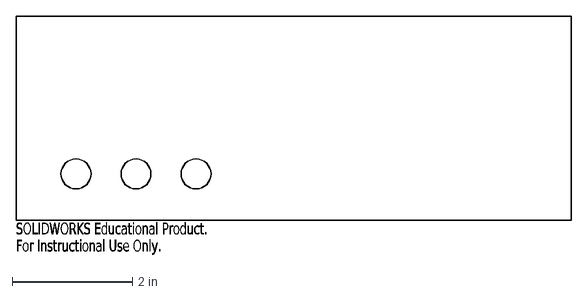
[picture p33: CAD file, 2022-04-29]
Enclosure Mk 4/DXF Files/Flat pattern - Back Plate.DXF
SOLIDWORKS Educational Product.
For Instructional Use Only.

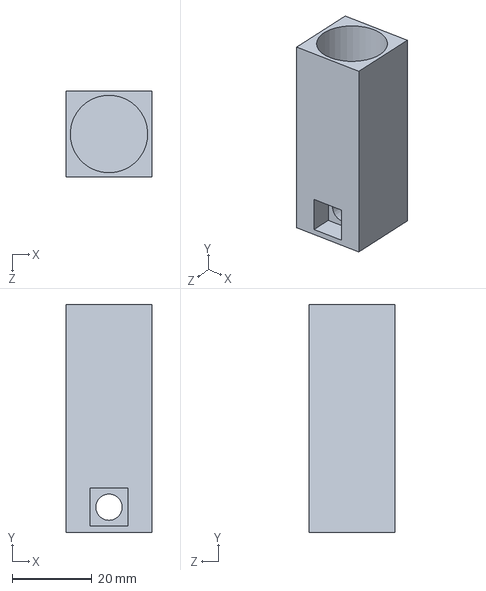
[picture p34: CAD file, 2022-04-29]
Enclosure Mk 4/Pendulum.SLDPRT
21.6 x 57.1 x 21.6 mm

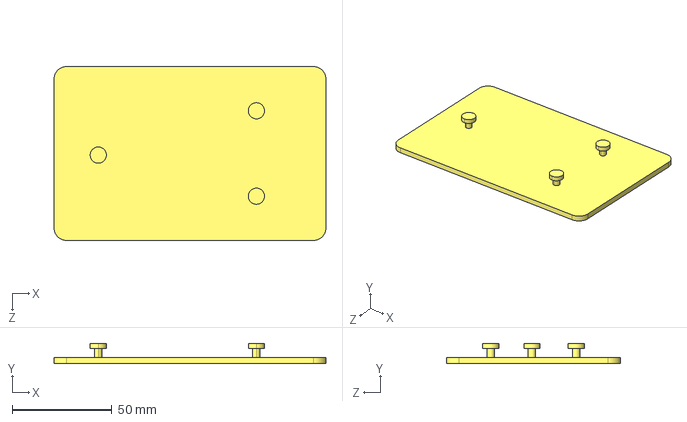
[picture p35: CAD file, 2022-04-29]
Enclosure Mk 4/3D Printed Parts/myRIO_Mounting_Plate.STEP
136.5 x 10.2 x 87.3 mm

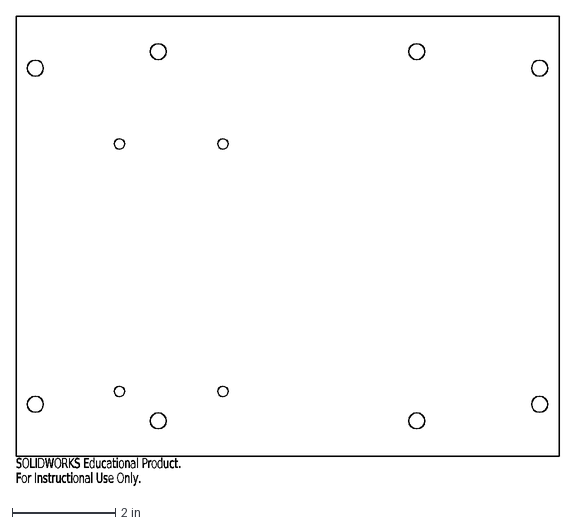
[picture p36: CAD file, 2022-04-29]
Enclosure Mk 4/DXF Files/Flat pattern - Base Plate.DXF
SOLIDWORKS Educational Product.
For Instructional Use Only.

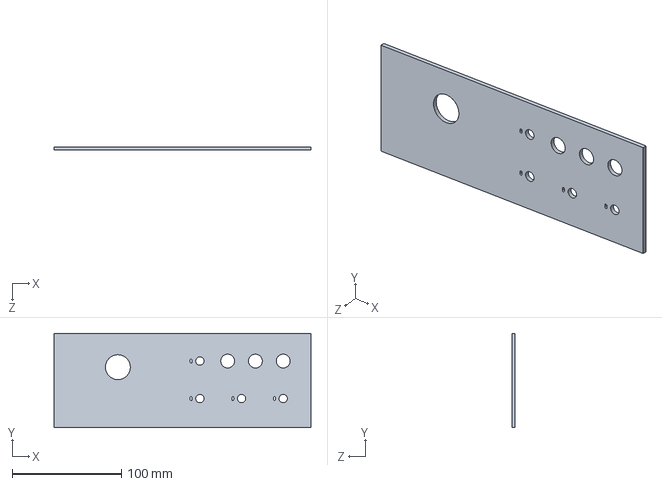
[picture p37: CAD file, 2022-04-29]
Enclosure Mk 4/Front and Back Piece.SLDPRT
235.0 x 86.4 x 3.17 mm

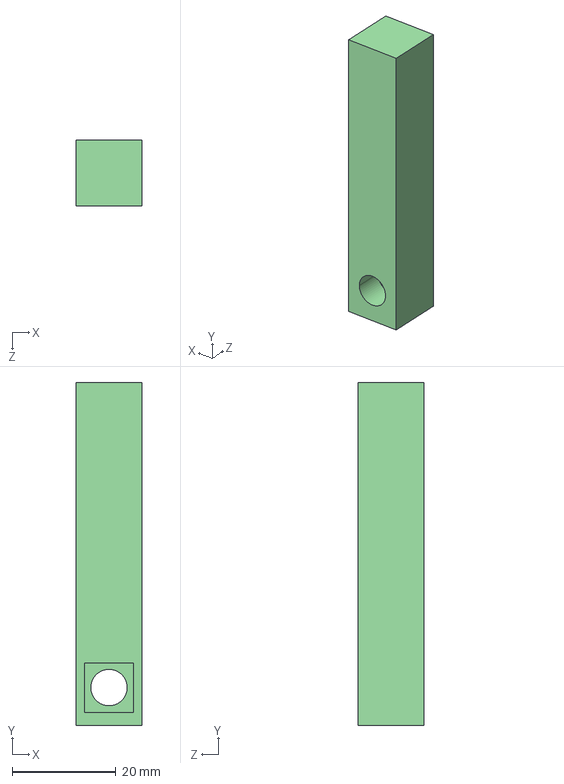
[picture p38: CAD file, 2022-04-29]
Enclosure Mk 4/3D Printed Parts/Pendulum.STEP
12.7 x 66.0 x 12.7 mm

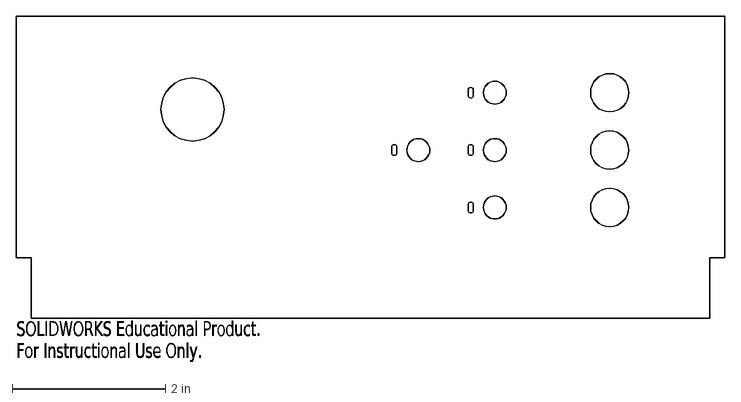
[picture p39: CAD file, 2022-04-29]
Enclosure Mk 4/DXF Files/Flat pattern - Front Plate (with Bend).DXF
SOLIDWORKS Educational Product.
For Instructional Use Only.

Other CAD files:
Enclosure Mk 4/myRIO_Mounting_Plate.STEP
Enclosure Mk 4/DXF Files/Flat pattern - Front Plate.DXF
Enclosure Mk 4/Power Supply Block.SLDPRT
Enclosure Mk 4/3D Printed Parts/Motor Mount.STL
Enclosure Mk 4/3D Printed Parts/Pendulum.STL
Enclosure Mk 4/3D Printed Parts/myRIO_Mounting_Plate.STL
Enclosure Mk 4/90272A163_Zinc-Plated Steel Pan Head Phillips Screw.SLDPRT
Enclosure Mk 4/90631A007_Low-Strength Steel Nylon-Insert Locknut.SLDPRT
Enclosure Mk 4/90640A129_Low-Strength Steel Nylon-Insert Locknut.SLDPRT
Enclosure Mk 4/90675A007_Steel Locknut with External-Tooth Lock Washer.SLDPRT
Enclosure Mk 4/91169A150_Steel Split Lock Washer.SLDPRT
Enclosure Mk 4/91274A103_Zinc-Aluminum-Coated Alloy Steel Socket Head Screw.SLDPRT
Enclosure Mk 4/91274A160_Zinc-Aluminum-Coated Alloy Steel Socket Head Screw.SLDPRT
Enclosure Mk 4/97467A725_18-8 Stainless Steel Heavy-Duty Rivet Nut.SLDPRT
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
